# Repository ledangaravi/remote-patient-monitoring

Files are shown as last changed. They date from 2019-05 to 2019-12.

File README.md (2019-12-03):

# Patient24

Welcome to the Patient24 Github Repository. To access detailed documentation about the project, please [go to the wiki](https://github.com/ledangaravi/remote-patient-monitoring/wiki).

## About
Patient24 brings together newly released sensors and state-of-the-art self-charging technology to provide next generation remote patient monitoring.

The Patient24 solution consists of a wearable device accompanied by an Android and an iOS application. [Watch the video](https://www.youtube.com/watch?v=plrVBWvTG4c) below to learn more.

Promotional Video (https://www.youtube.com/watch?v=plrVBWvTG4c)

## Contact
- For all enquiries do not hesitate to [contact us via email](mailto:jf1116@ic.ac.uk).

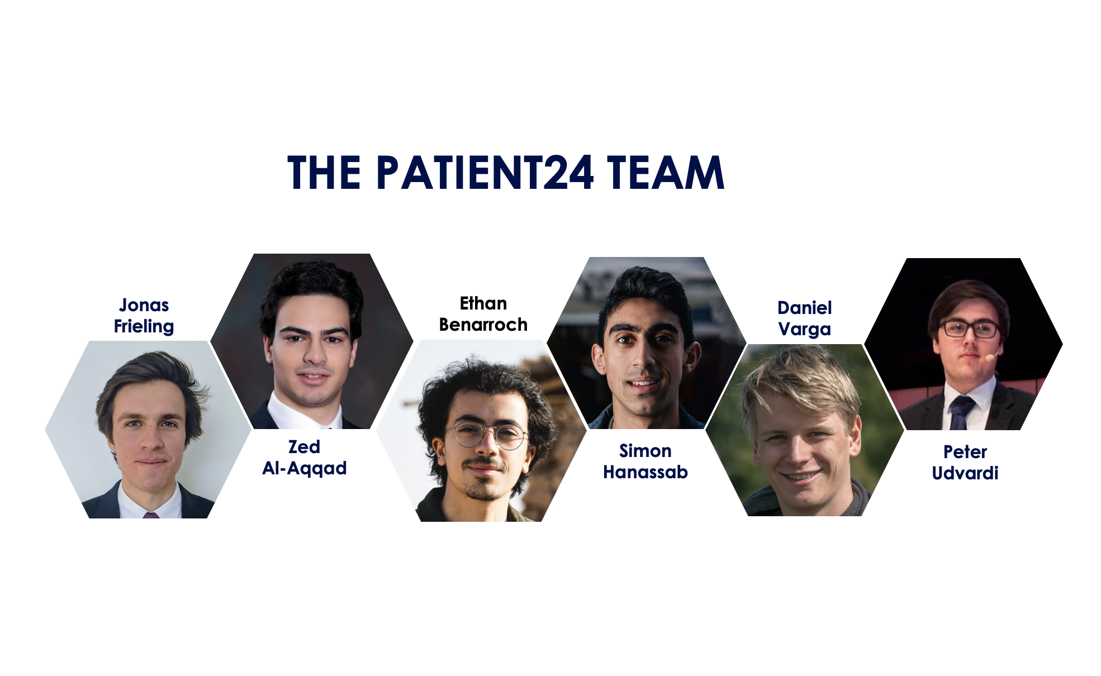
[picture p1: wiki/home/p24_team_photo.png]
Team Photo


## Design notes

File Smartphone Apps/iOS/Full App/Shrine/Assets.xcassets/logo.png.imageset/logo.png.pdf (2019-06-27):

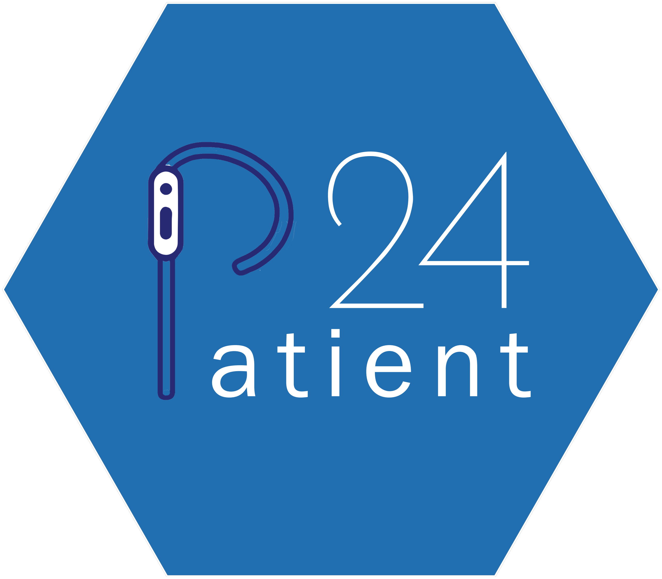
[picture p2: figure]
atient

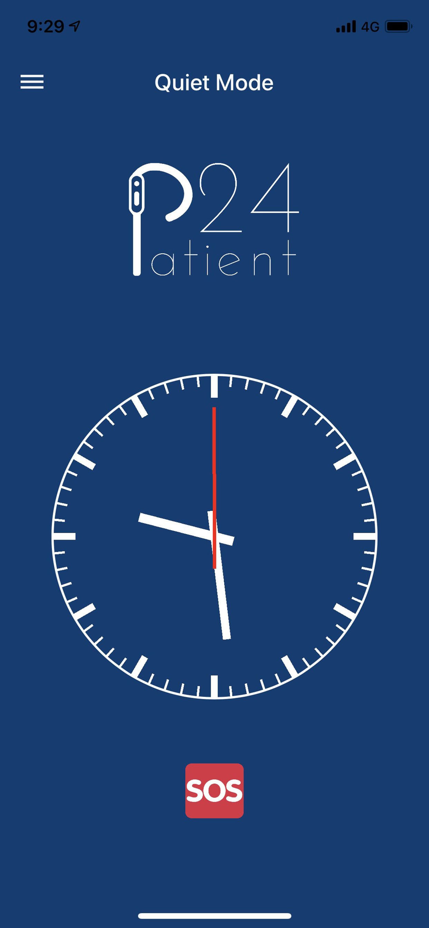
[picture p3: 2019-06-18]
Marketing/poster/images/iphone_screenshot.jpg

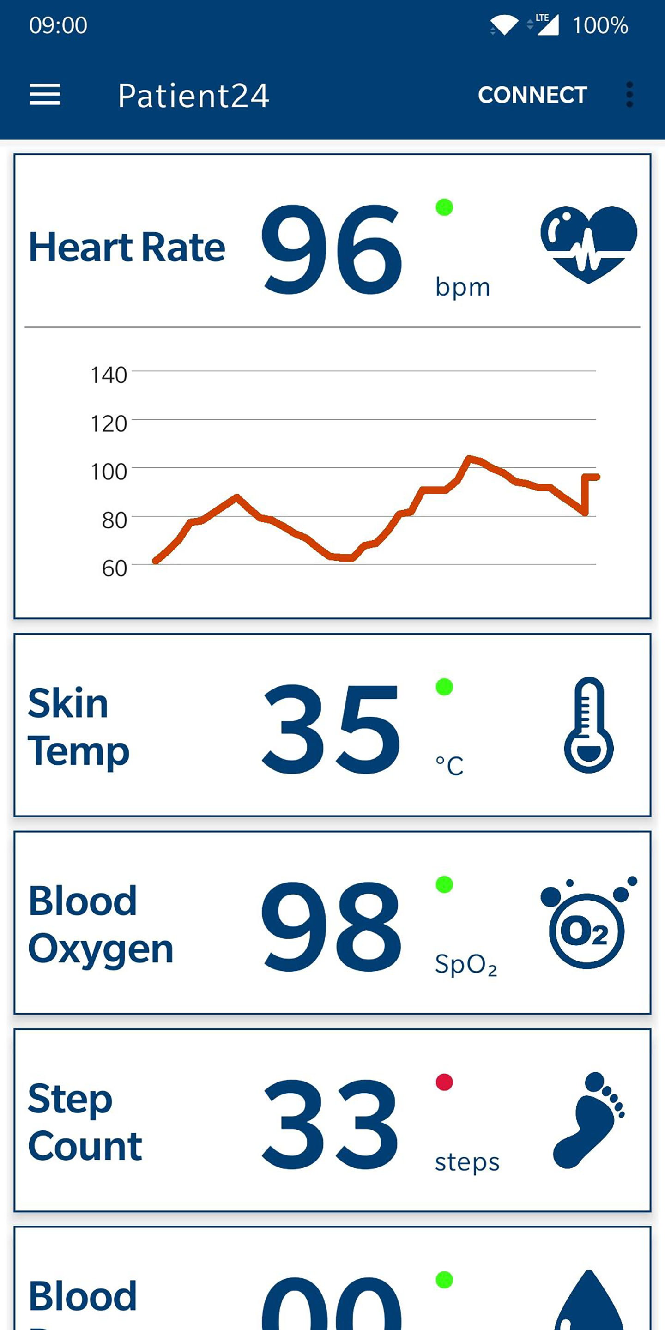
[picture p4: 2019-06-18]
Marketing/poster/images/android.jpg

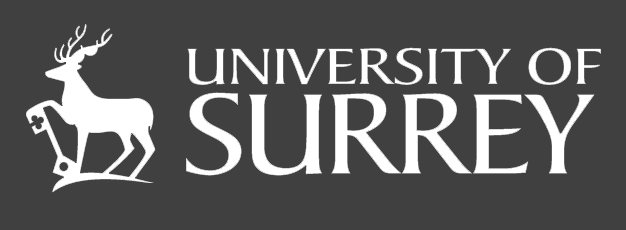
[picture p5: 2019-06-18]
Marketing/poster/images/surrey-Uni.png

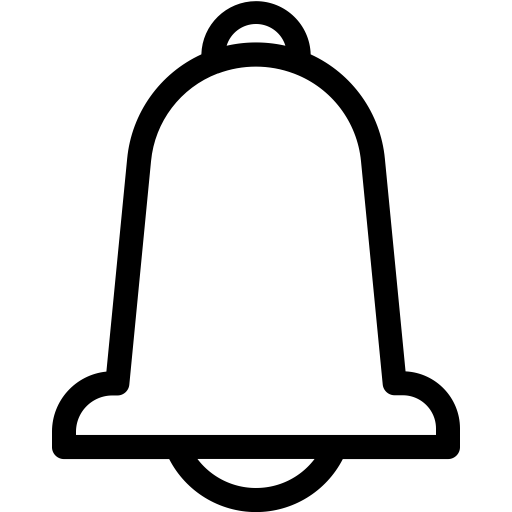
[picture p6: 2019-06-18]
Marketing/poster/images/alert.png

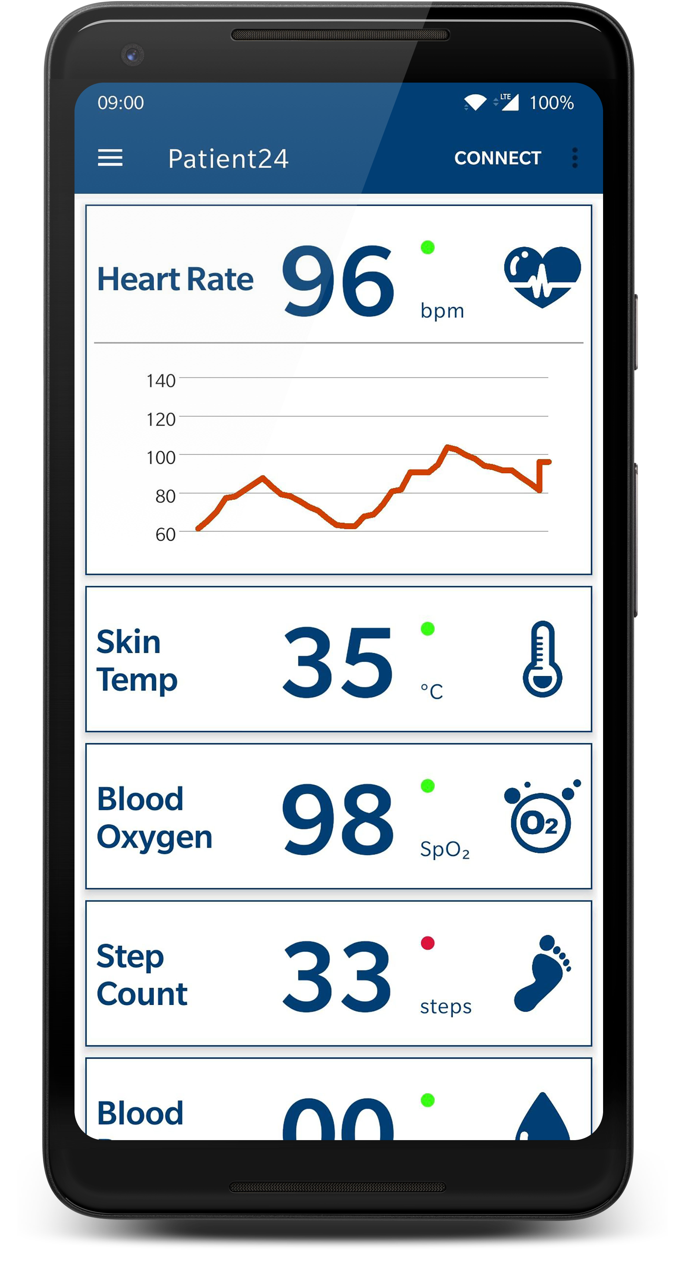
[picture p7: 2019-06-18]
Marketing/poster/images/android_framed.png

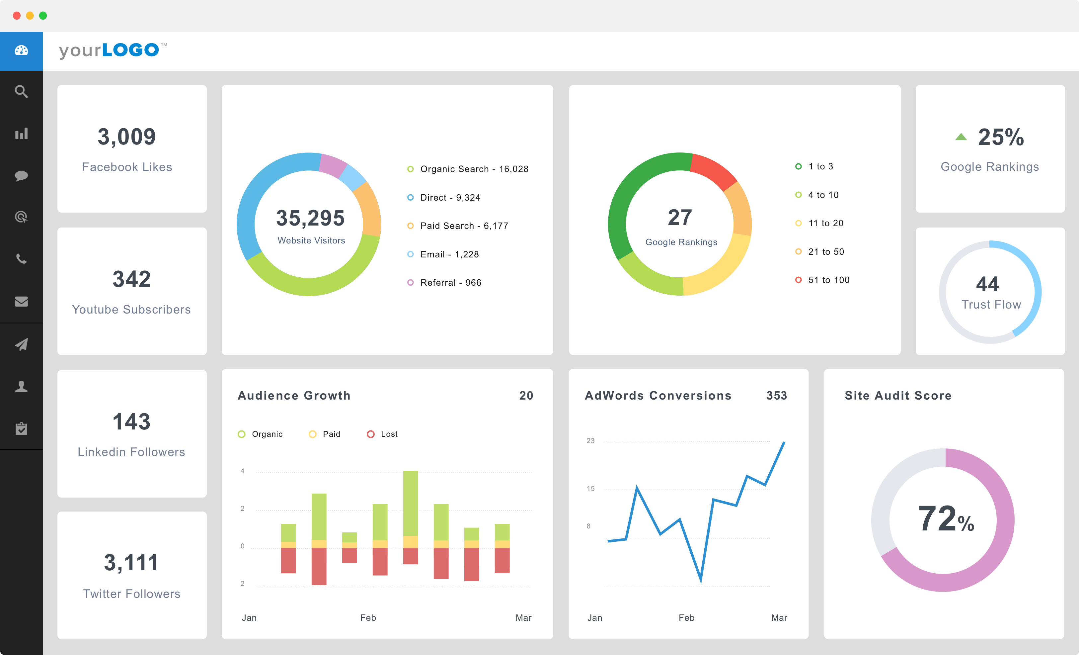
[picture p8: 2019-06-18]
Marketing/poster/images/dashboard.png

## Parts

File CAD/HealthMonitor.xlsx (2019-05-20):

Id | Designator | Package | Quantity | Designation | Tolerance
1 | J6 | USB_C_Receptacle_Amphenol_12401610E4-2A_CircularHoles | 1 | USB_C_Receptacle_USB2.0
2 | U9 | MAX86141ENP | 1 | MAX86141ENP+
4 | D8,D6 | VEMD5010X01 | 2 | VEMD5010X01
6 | U12 | QFN-24-1EP_4x4mm_P0.5mm_EP2.6x2.6mm | 1 | CP2102N-A01-GQFN24
7 | U6 | PQFN50P300X300X86-16N | 1 | LSM6DS33TR
17 | U5 | PQFN70P280X280X100-10N | 1 | BH1792GLC
18 | U10 | TSSOP-8_4.4x3mm_P0.65mm | 1 | AT24CS02-XHM
19 | R32,R23,R24,R25,R35,R33,R11,R10,R9,Rpu1,Rpu2 | R_0402_1005Metric | 11 | 10k
20 | U7 | Texas_R_PUQFN-N12 | 1 | TXB0104RUT
21 | C17,C27 | C_0603_1608Metric | 2 | 22u
23 | C26,C24,C25,C7,C20,C21,C23,C5 | C_0402_1005Metric | 8 | 1u
24 | D7 | LED_PLCC-2 | 1 | LED_LY_P47F-TM
25 | D5 | LED_PLCC-2 | 1 | LED-LT PWSG-AABB-36-46-F
29 | R6 | R_0402_1005Metric | 1 | 1M
30 | U4 | SOT-23-5 | 1 | LD39015M33R
31 | U13 | ADG884BRMZ | 1 | ADG884BRMZ
32 | U2 | ADP5092ACPZ-1-R7 | 1 | ADP5092ACPZ-1-R7
33 | Y1 | XTAL_ABS06-32.768KHZ-T | 1 | ABS06-32.768KHZ-T
34 | C22,C1,C13,C11,C9 | C_0402_1005Metric | 5 | 0.1u
35 | C6,C12,C16 | C_0402_1005Metric | 3 | 4.7u
39 | C14 | C_0402_1005Metric | 1 | 5600p
40 | C15,C2,C3,C10 | C_0402_1005Metric | 4 | 10u
41 | C18,C19 | C_0402_1005Metric | 2 | 12p
47 | D1 | D_0603_1608Metric | 1 | LED_ir
48 | D2,D3 | D_0603_1608Metric | 2 | LED_green
49 | L2 | L_0603_1608Metric | 1 | 4.7u
50 | R20 | R_0402_1005Metric | 1 | 2.4k
51 | R22 | R_0402_1005Metric | 1 | 412k
52 | R26,R27,R29,R30,R28 | R_0402_1005Metric | 5 | 50k
53 | R19,R16 | R_0402_1005Metric | 2 | 3.32M | 1%
54 | R31 | R_0402_1005Metric | 1 | 4.75k
55 | R34 | R_0402_1005Metric | 1 | 6.6k
57 | R21,R17 | R_0402_1005Metric | 2 | 6.65M | 1%
58 | D4 | DIOC0404X01-4N | 1 | SML-LX0404SIUPGUSB
59 | U3 | LTC4079IDD-PBF | 1 | LTC4079IDD-PBF
60 | U1 | MAX17048G+ | 1 | MAX17048G+T10
61 | U8 | MAX1921EUT18&plus_T | 1 | MAX1921EUT18+
62 | C4 | C_0402_1005Metric | 1 | 10n
63 | FB1 | L_0402_1005Metric | 1 | Ferrite_Bead
64 | R13,R12 | R_0402_1005Metric | 2 | 5M | 1%
65 | R14 | R_0402_1005Metric | 1 | 3.01M | 1%
66 | R15 | R_0402_1005Metric | 1 | 6.98M | 1%
67 | R18 | R_0402_1005Metric | 1 | 1.07M | 1%
68 | R7 | R_0402_1005Metric | 1 | 2M | 1%
69 | R8 | R_0402_1005Metric | 1 | 3.3k
70 | R5 | R_0402_1005Metric | 1 | 3.57M | 1%
71 | R4 | R_0402_1005Metric | 1 | 6.49M | 1%
72 | R3,R1 | R_0402_1005Metric | 2 | 4M | 1%
73 | R2 | R_0402_1005Metric | 1 | 55.6k | 1%
74 | L1 | L_0805_2012Metric | 1 | 22u

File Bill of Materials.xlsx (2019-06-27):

Designator | Package | Quantity | Designation | Model Number | Supplier | College Discount? | Unit Price (inc VAT) | Unit Price (exc VAT) | Total Quantity with Discount applied (exc VAT) | Scaled Unit Price (inc VAT) | Scaled with Total Quantity & Discounts
C12,C16,C6 | C_0402_1005Metric | 3 | 4.7uF | C1005X5R0J475M050BC | Farnell | 19% | £0.1960 | £0.1568 | £0.3810 | £0.0267 | £0.0649
C14 | C_0402_1005Metric | 1 | 5600pF | MC0402B562K160CT | Farnell | 19% | £0.0090 | £0.0072 | £0.0058 | £0.0033 | £0.0027
C15,C2,C3 | C_0402_1005Metric | 3 | 10uF | GRM155R60J106ME44D | Farnell | 19% | £0.8320 | £0.6656 | £1.6174 | £0.0757 | £0.1840
C17,C27 | C_0603_1608Metric | 2 | 22uF | GRM188R61A226ME15D | Farnell | 19% | £0.2300 | £0.1840 | £0.2981 | £0.0433 | £0.0701
C22,C13,C11, C10, C9, C1 | C_0402_1005Metric | 6 | 0.1uF | 0402YC104KAT2A | Farnell | 19% | £0.0404 | £0.0323 | £0.1571 | £0.0061 | £0.0296
C29,C30,C18,C19 | C_0402_1005Metric | 4 | 12pF | MC0402N120J500CT | Farnell | 19% | £0.0209 | £0.0167 | £0.0542 | £0.0033 | £0.0107
C4 | C_0402_1005Metric | 1 | 10nF | 04023C103KAT2A | Farnell | 19% | £0.0352 | £0.0282 | £0.0228 | £0.0051 | £0.0041
C7,C20,C21,C23,C26,C8,C28,C24,C25,C5 | C_0402_1005Metric | 10 | 1uF | 0402ZD105KAT2A | Farnell | 19% | £0.1840 | £0.1472 | £1.1923 | £0.0423 | £0.3426
D1 | D_0603_1608Metric | 1 | LED_ir | TAN1111C | RS | 19% | £0.1000 | £0.0800 | £0.0648 | £0.0568 | £0.0460
D2,D3 | D_0603_1608Metric | 2 | LED_green | 404-1005-1-ND | DigiKey | 0% | £0.6400 | £0.5120 | £1.0240 | £0.0780 | £0.1560
D4 | DIOC0404X01-4N | 1 | SML-LX0404SIUPGUSB | SML-LX0404SIUPGUSB | Mouser | 0% | £0.7850 | £0.6280 | £0.6280 | £0.2310 | £0.2310
D5 | LED_PLCC-2 | 1 | LED-LT PWSG-AABB-36-46-F | VAOL-S2YP4 | Mouser | 0% | £0.4190 | £0.3352 | £0.3352 | £0.1290 | £0.1290
D7 | LED_PLCC-2 | 1 | LED_LY_P47F-TM | LT T66G-BBDA-29-0-20-R33-Z | DigiKey | 0% | £0.4700 | £0.3760 | £0.3760 | £0.1600 | £0.1600
D8,D6 | VEMD5010X01 | 2 | VEMD5010X01 | VEMD5010X01 | RS | 19% | £0.5200 | £0.4160 | £0.6739 | £0.3064 | £0.4964
FB1 | L_0402_1005Metric | 1 | Ferrite_Bead | MPZ1005A331ETD25 | Mouser | 0% | £0.1830 | £0.1464 | £0.1464 | £0.0480 | £0.0480
J27 | Molex - 51281-0594-MOLEX_51281-0594_0 | 1 | 51281-0594 | 51281-0594 | Farnell | 19% | £0.3100 | £0.2480 | £0.2009 | £0.1600 | £0.1296
J6 | USB_C_Receptacle_Amphenol_12401610E4-2A | 1 | USB_C_Receptacle_USB2.0 | 12401610E4#2A | Mouser | 0% | £1.6400 | £1.3120 | £1.3120 | £0.9350 | £0.9350
L1 | L_0805_2012Metric | 1 | 22uH | MLZ2012M220WT000 | Mouser | 0% | £0.1070 | £0.0856 | £0.0856 | £0.0280 | £0.0280
L2 | L_0603_1608Metric | 1 | 4.7uH | KLZ1608MHR4R7WTD25 | Mouser | 0% | £0.1900 | £0.1520 | £0.1520 | £0.0540 | £0.0540
R13,R12 | R_0402_1005Metric | 2 | 4.99MΩ | CRCW04024M99FKEDC | Mouser | 0% | £0.1000 | £0.0800 | £0.1600 | £0.0030 | £0.0060
R14 | R_0402_1005Metric | 1 | 3.01MΩ | CRCW04023M01FKED | Farnell | 19% | £0.0091 | £0.0073 | £0.0059 | £0.0020 | £0.0016
R15 | R_0402_1005Metric | 1 | 6.98MΩ | CRCW04026M98FKED | Mouser | 0% | £0.0760 | £0.0608 | £0.0608 | £0.0030 | £0.0030
R18 | R_0402_1005Metric | 1 | 1.07MΩ | RC0402FR-071M07L | Mouser | 0% | £0.0760 | £0.0608 | £0.0608 | £0.0030 | £0.0030
R19,R16 | R_0402_1005Metric | 2 | 3.32MΩ | CRCW04023M32FKED | Mouser | 0% | £0.0720 | £0.0576 | £0.1152 | £0.0030 | £0.0060
R2 | R_0402_1005Metric | 1 | 56kΩ | CRCW04023M32FKED | Farnell | 19% | £0.0760 | £0.0608 | £0.0492 | £0.0030 | £0.0024
R20 | R_0402_1005Metric | 1 | 2.4kΩ | CRCW04022K40FKED | Farnell | 19% | £0.0168 | £0.0134 | £0.0109 | £0.0035 | £0.0028
R21,R17 | R_0402_1005Metric | 2 | 6.65MΩ | CRCW04026M65FKED | Farnell | 19% | £0.0119 | £0.0095 | £0.0154 | £0.0033 | £0.0053
R22 | R_0402_1005Metric | 1 | 412kΩ | CRCW0402412KFKED | Farnell | 19% | £0.0166 | £0.0133 | £0.0108 | £0.0035 | £0.0028
R26,R27,R29,R30,R28 | R_0402_1005Metric | 5 | 50kΩ | CRCW040250K0FKED | Mouser | 0% | £0.4190 | £0.3352 | £1.6760 | £0.0810 | £0.4050
R3,R1 | R_0402_1005Metric | 2 | 4MΩ | CRCW04023M92FKED | Mouser | 0% | £0.0760 | £0.0608 | £0.1216 | £0.0030 | £0.0060
R31 | R_0402_1005Metric | 1 | 4.75kΩ | CRCW04024K75FKED | Farnell | 19% | £0.0089 | £0.0071 | £0.0058 | £0.0044 | £0.0036
R33,R24,R25,R32,R23,R35,R11,R10,R9, Rpu1, Rpu2 | R_0402_1005Metric | 11 | 10kΩ | CRCW040210K0FKEDHP | Farnell | 19% | £0.0418 | £0.0334 | £0.2980 | £0.0099 | £0.0882
R34 | R_0402_1005Metric | 1 | 6.65kΩ | MCWR04X6651FTL | Farnell | 19% | £0.0041 | £0.0033 | £0.0027 | £0.0006 | £0.0005
R4 | R_0402_1005Metric | 1 | 6.49MΩ | RC0402FR-076M49L | Mouser | 0% | £0.0760 | £0.0608 | £0.0608 | £0.0020 | £0.0020
R5 | R_0402_1005Metric | 1 | 3.57M | CRCW04023M57FKED | Farnell | 19% | £0.0088 | £0.0070 | £0.0057 | £0.0027 | £0.0022
R6 | R_0402_1005Metric | 1 | 1MΩ | MCMR04X1004FTL | Farnell | 19% | £0.0085 | £0.0068 | £0.0055 | £0.0013 | £0.0011
R7 | R_0402_1005Metric | 1 | 2MΩ | CRCW04022M00FKED | Farnell | 19% | £0.0168 | £0.0134 | £0.0109 | £0.0035 | £0.0028
R8 | R_0402_1005Metric | 1 | 3.3kΩ | CRCW04023K30FKED | Farnell | 19% | £0.0146 | £0.0117 | £0.0095 | £0.0031 | £0.0025
U1 | MAX17048G+ | 1 | MAX17048G+T10 | MAX17048G+T10 | Farnell | 19% | £1.9100 | £1.5280 | £1.2377 | £0.9340 | £0.7565
U10 | TSSOP-8_4.4x3mm_P0.65mm | 1 | AT24CS02-XHM | AT24CS02-XHM | Mouser | 0% | £0.1680 | £0.1344 | £0.1344 | £0.1650 | £0.1650
U11 | BT832-BT832L | 1 | BT832L | BT832L | Mouser | 0% | £7.2600 | £5.8080 | £5.8080 | £3.8900 | £3.8900
U12 | QFN-24-1EP_4x4mm_P0.5mm_EP2.6x2.6mm | 1 | CP2102N-A01-GQFN24 | CP2102N-A01-GQFN24 | Farnell | 19% | £1.2400 | £0.9920 | £0.8035 | £0.9320 | £0.7549
U13 | ADG884BRMZ | 1 | ADG884BRMZ | ADG884BRMZ | Farnell | 19% | £2.4800 | £1.9840 | £1.6070 | £1.2400 | £1.0044
U14,U4 | SOT-23-5 | 2 | LD39015M33R | LD39015M33R | Farnell | 19% | £0.6860 | £0.5488 | £0.8891 | £0.2810 | £0.4552
U2 | ADP5092ACPZ-1-R7 | 1 | ADP5092ACPZ-1-R7 | ADP5092ACPZ-1-R7 | Farnell | 19% | £2.5200 | £2.0160 | £1.6330 | £2.4000 | £1.9440
U3 | LTC4079IDD-PBF | 1 | LTC4079IDD-PBF | LTC4079IDD-PBF | Mouser | 0% | £5.0000 | £4.0000 | £4.0000 | £2.5400 | £2.5400
U5 | PQFN70P280X280X100-10N | 1 | BH1792GLC | BH1792GLC | Mouser | 0% | £8.1500 | £6.5200 | £6.5200 | £4.2900 | £4.2900
U6 | PQFN50P300X250X86-14N | 1 | LSM6DSLTR | LSM6DSLTR | Mouser | 0% | £3.0400 | £2.4320 | £2.4320 | £1.4900 | £1.4900
U7 | Texas_R_PUQFN-N12 | 1 | TXB0104RUT | TXB0104RUT | Mouser | 0% | £1.0600 | £0.8480 | £0.8480 | £0.4230 | £0.4230
U8 | MAX1921EUT18&plus_T | 1 | MAX1921EUT18+ | MAX1921EUT18+ | Farnell | 19% | £2.3300 | £1.8640 | £1.5098 | £1.3300 | £1.0773
U9 | MAX86141ENP | 1 | MAX86141ENP+ | MAX86141ENP+ | Farnell | 19% | £5.8900 | £4.7120 | £3.8167 | £2.9300 | £2.3733
X1 | LiPo Battery | 1 | LP-402025-IS-3 | LP-402025-IS-3 | Farnell | 19% | £15.3300 | £12.2640 | £9.9338 | £6.5700 | £5.3217
X2 | Peltier Module | 1 | CP-85138 | CP-85138 | Mouser | 0% | £11.4400 | £9.1520 | £9.1520 | £9.0900 | £9.0900
X3 | Heat Sink | 1 | MPC151525T | MPC151525T | Farnell | 19% | £1.7700 | £1.4160 | £1.1470 | £0.6280 | £0.5087
Y1 | XTAL_ABS06-32.768KHZ-T | 1 | ABS06-32.768KHZ-T | ABS06-32.768KHZ-T | Farnell | 19% | £1.2100 | £0.9680 | £0.7841 | £0.5470 | £0.4431
 |  |  |  |  |  |  | £79.52 | £63.62 | £63.67 | £42.21 | £40.20
NB: Prices valid as of 22/06/2019 |  |  |  |  |  |  |  |  |  |  | exc VAT:
 |  |  |  |  |  |  |  |  |  |  | £32.16

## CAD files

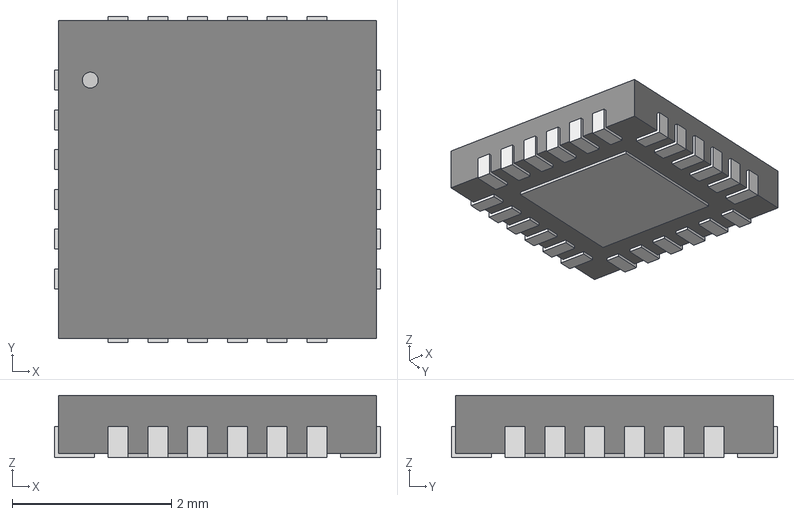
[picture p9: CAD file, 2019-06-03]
CAD/3dmodels/ADP5092.step
4.10 x 4.10 x 0.783 mm

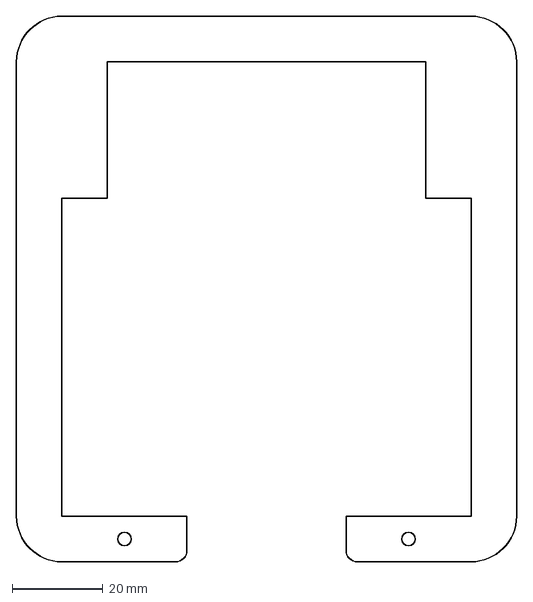
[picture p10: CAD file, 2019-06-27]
PCB/bracket/bracket_top.dxf
110.0 x 120.0 mm

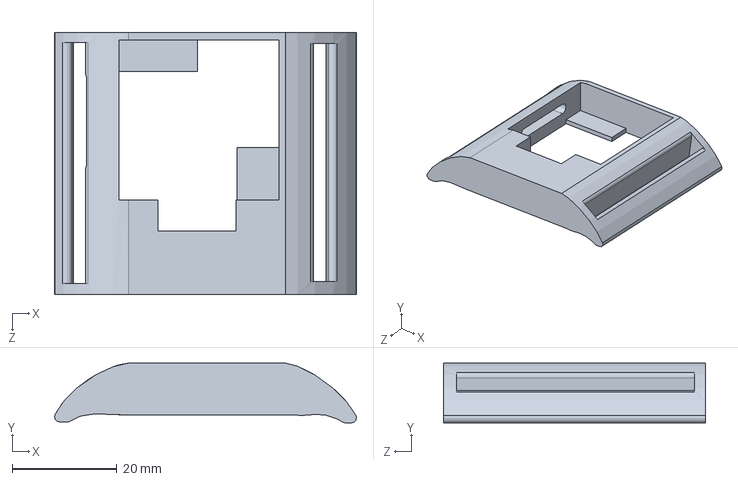
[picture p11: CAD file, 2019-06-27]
Strap Design/Solidworks Files/Version5_SensorPCB.SLDPRT
57.6 x 11.4 x 50.0 mm

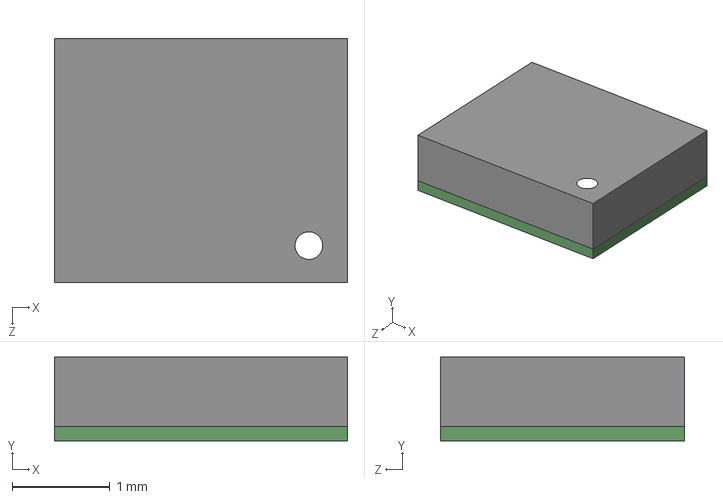
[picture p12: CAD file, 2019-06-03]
CAD/3dmodels/LSM6DS3--3DModel-STEP-56544.STEP
3.00 x 0.86 x 2.50 mm

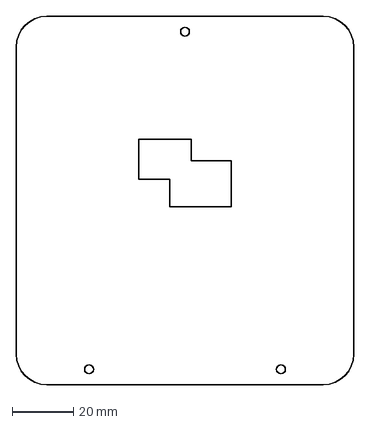
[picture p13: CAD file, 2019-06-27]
PCB/bracket/bracket_bottom.dxf
110.0 x 120.0 mm

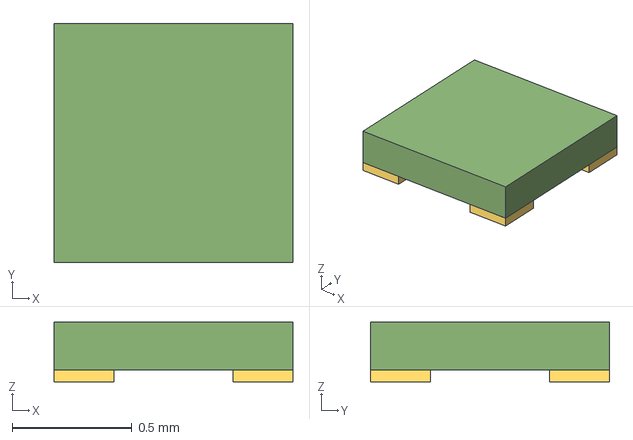
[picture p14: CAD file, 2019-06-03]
CAD/3dmodels/LMS_XL0404.step
1.00 x 1.00 x 0.25 mm

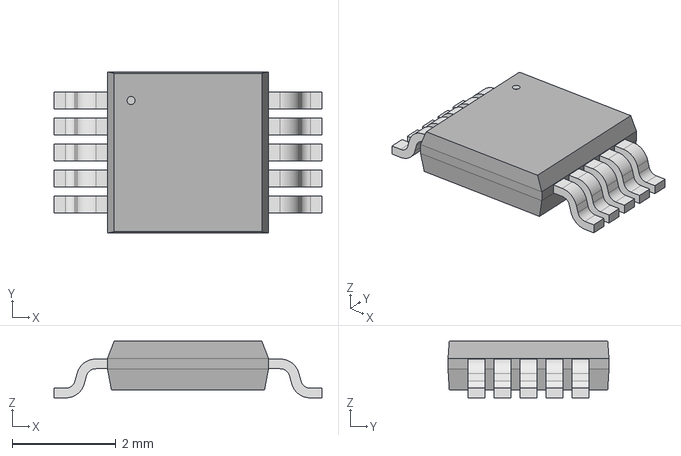
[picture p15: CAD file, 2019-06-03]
CAD/3dmodels/ADG884BRMZ.step
5.16 x 3.10 x 1.09 mm

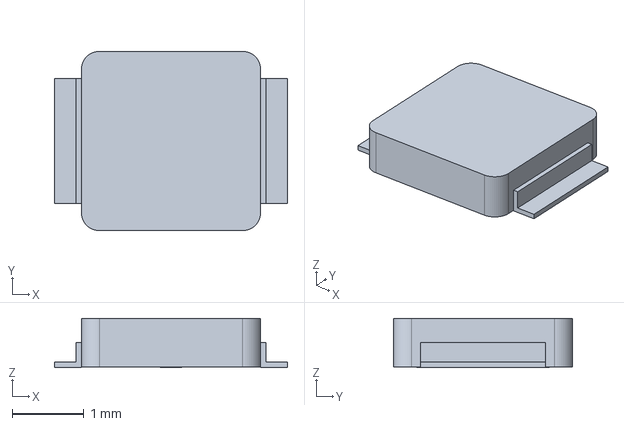
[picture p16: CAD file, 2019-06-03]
CAD/3dmodels/LED_LY_P47F-v2.step
3.25 x 2.50 x 0.685 mm

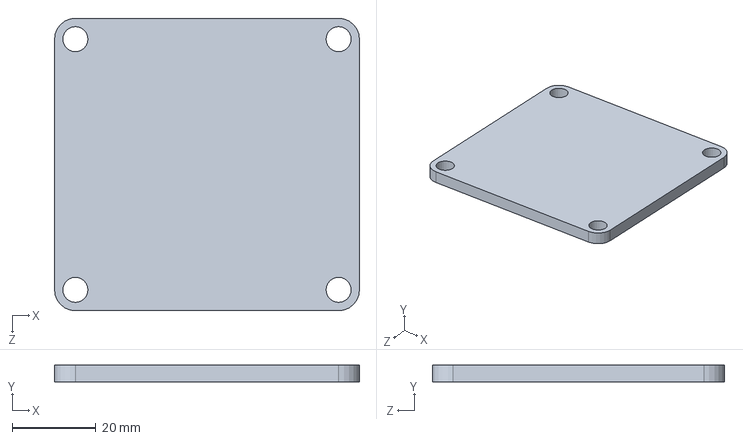
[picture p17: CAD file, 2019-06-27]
Strap Design/Solidworks Files/Mould4_BatteryTop.SLDPRT
73.0 x 4.00 x 70.0 mm

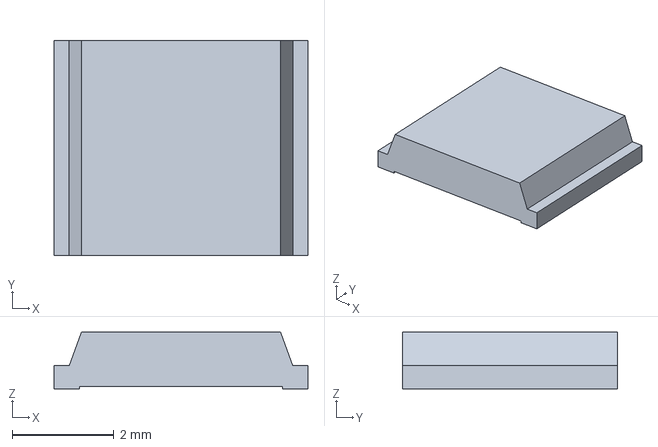
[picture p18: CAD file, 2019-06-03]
CAD/3dmodels/VEMD5010.step
5.00 x 4.24 x 1.12 mm

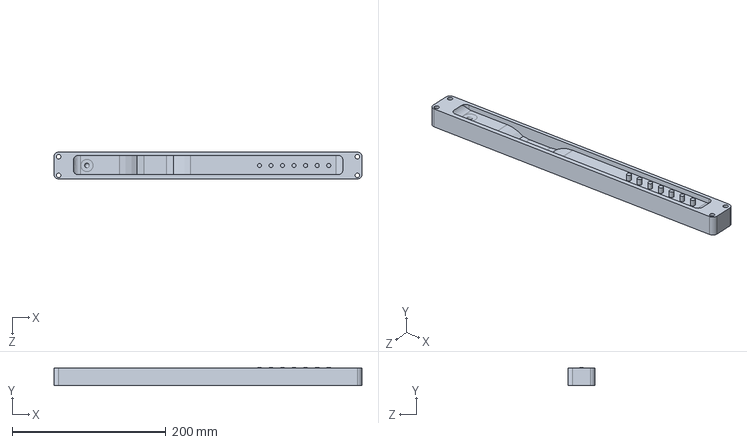
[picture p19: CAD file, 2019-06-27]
Strap Design/Solidworks Files/Mould1_part1.SLDPRT
400.0 x 24.0 x 35.0 mm

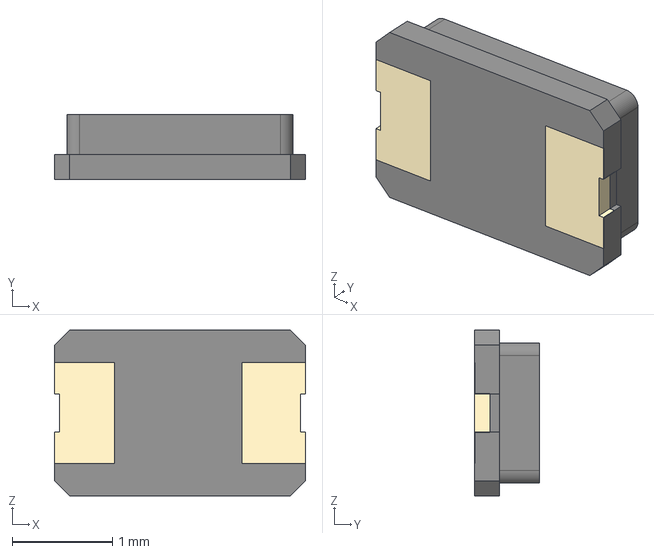
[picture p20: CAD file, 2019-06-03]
CAD/3dmodels/ABS06-v2.step
2.50 x 0.648 x 1.65 mm

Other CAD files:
Strap Design/Solidworks Files/Mould2_part1.SLDPRT
Strap Design/Solidworks Files/Mould1_part2.SLDPRT
Strap Design/Solidworks Files/Mould4_SensorBottom.SLDPRT
Strap Design/Solidworks Files/Mould3_part2.SLDPRT
Strap Design/Solidworks Files/Mould4_SensorTop.SLDPRT
CAD/3dmodels/BT832L.STEP
CAD/3dmodels/LTC4079.step
CAD/3dmodels/MAX86141.step
CAD/3dmodels/max1921.step
Strap Design/Solidworks Files/Mould2_part2.SLDPRT
Strap Design/Solidworks Files/Mould3_part1.SLDPRT
Strap Design/Solidworks Files/Mould4_BatteryBottom.SLDPRT
Strap Design/Solidworks Files/SENSORMODULEP24.SLDDRW
Strap Design/Solidworks Files/Version5_Batt,Peltier,PowerPCB.SLDPRT
Strap Design/Solidworks Files/Version6_powerModule.SLDPRT
Strap Design/Solidworks Files/Version6_sensorModule.SLDPRT
Strap Design/Solidworks Files/powPCB+peletierbattVersion5flat.SLDDRW

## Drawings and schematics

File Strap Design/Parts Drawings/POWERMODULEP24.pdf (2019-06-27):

2 1

B

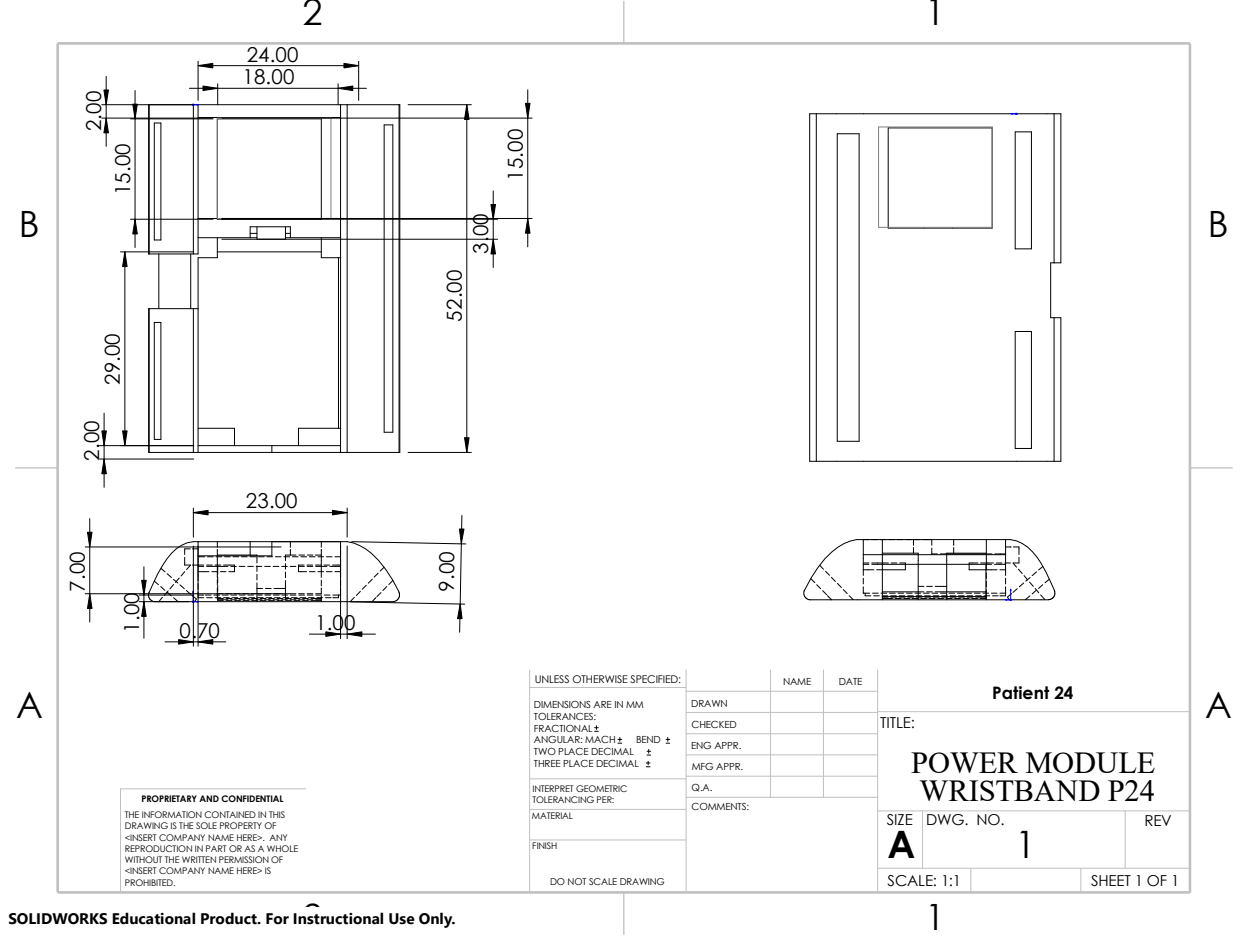
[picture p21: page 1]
SIZE; BEND; DWG. NO.; A DRAWN; COMMENTS:; PROHIBITED.; SHEET 1 OF 1; DATE; MATERIAL; NAME; REV; DO NOT SCALE DRAWING; SCALE: 1:1; FINISH; Patient 24

UNLESS OTHERWISE SPECIFIED:

DIMENSIONS ARE IN MM
TOLERANCES:
FRACTIONAL
ANGULAR: MACH
TWO PLACE DECIMAL

CHECKED | | TITLE: WRISTBAND P24

MFG APPR. | | POWER MODULE THREE PLACE DECIMAL

ENG APPR.

INTERPRET GEOMETRIC TOLERANCING PER: | Q.A.

PROPRIETARY AND CONFIDENTIAL
THE INFORMATION CONTAINED IN THIS
DRAWING IS THE SOLE PROPERTY OF
<INSERT COMPANY NAME HERE>. ANY
REPRODUCTION IN PART OR AS A WHOLE
WITHOUT THE WRITTEN PERMISSION OF
<INSERT COMPANY NAME HERE> IS

SOLIDWORKS Educational Product. For Instructional Use Only.

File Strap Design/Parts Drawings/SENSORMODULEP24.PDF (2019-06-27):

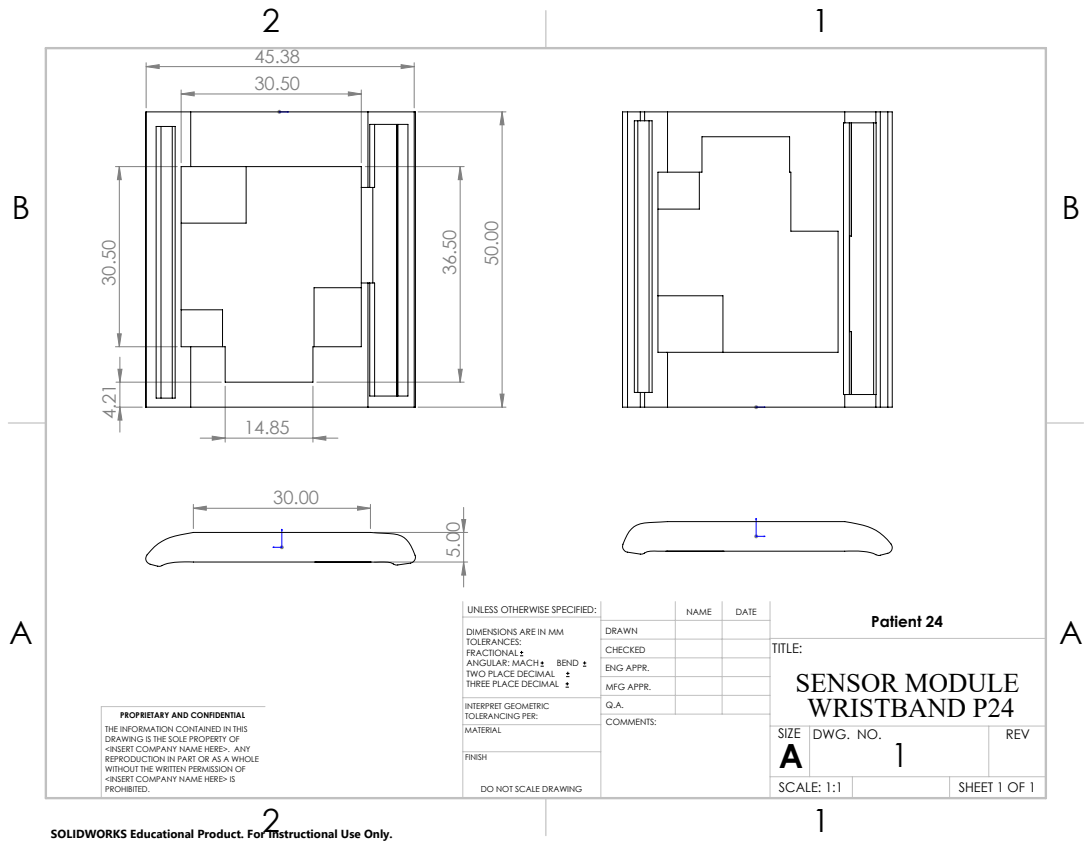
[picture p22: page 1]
DWG. NO.; DO NOT SCALE DRAWING; SCALE: 1:1; SHEET 1 OF 1; Patient 24

UNLESS OTHERWISE SPECIFIED:

DIMENSIONS ARE IN MM TOLERANCES: FRACTIONAL ANGULAR: MACH BEND TWO PLACE DECIMAL THREE PLACE DECIMAL | DRAWN

CHECKED | | TITLE: SENSOR MODULE WRISTBAND P24

ENG APPR.
MFG APPR.

INTERPRET GEOMETRIC TOLERANCING PER: | Q.A.

PROPRIETARY AND CONFIDENTIAL
THE INFORMATION CONTAINED IN THIS
DRAWING IS THE SOLE PROPERTY OF
<INSERT COMPANY NAME HERE>. ANY
REPRODUCTION IN PART OR AS A WHOLE
WITHOUT THE WRITTEN PERMISSION OF
<INSERT COMPANY NAME HERE> IS
PROHIBITED.

SOLIDWORKS Educational Product. For Instructional Use Only.

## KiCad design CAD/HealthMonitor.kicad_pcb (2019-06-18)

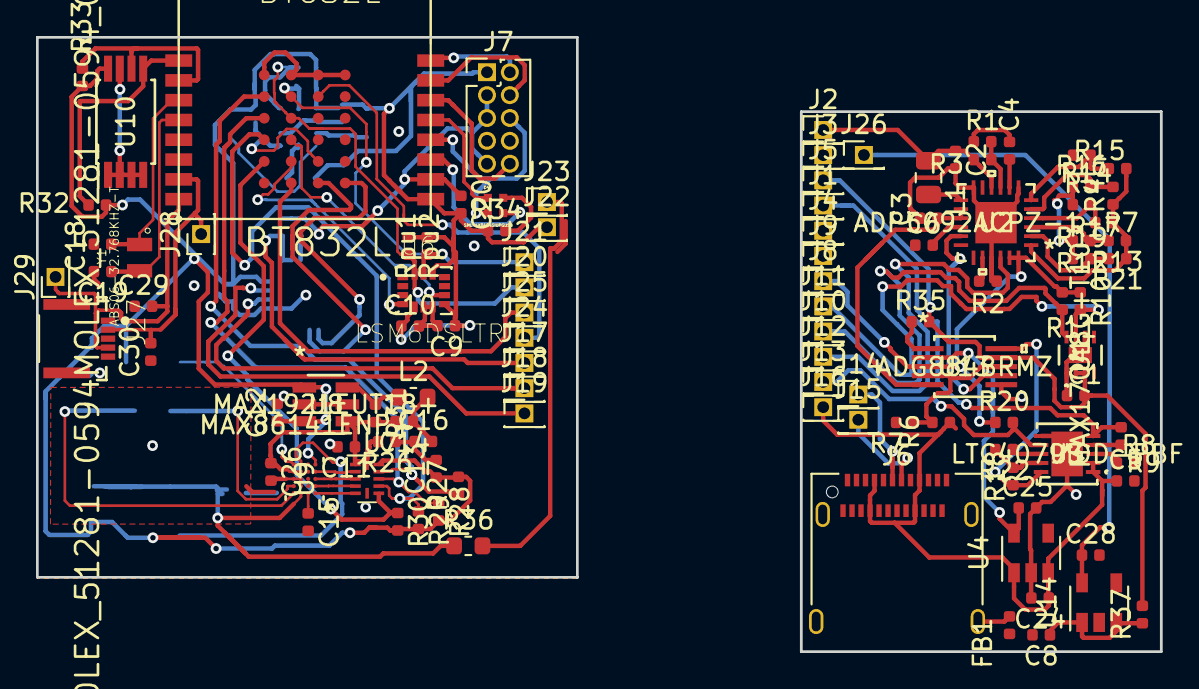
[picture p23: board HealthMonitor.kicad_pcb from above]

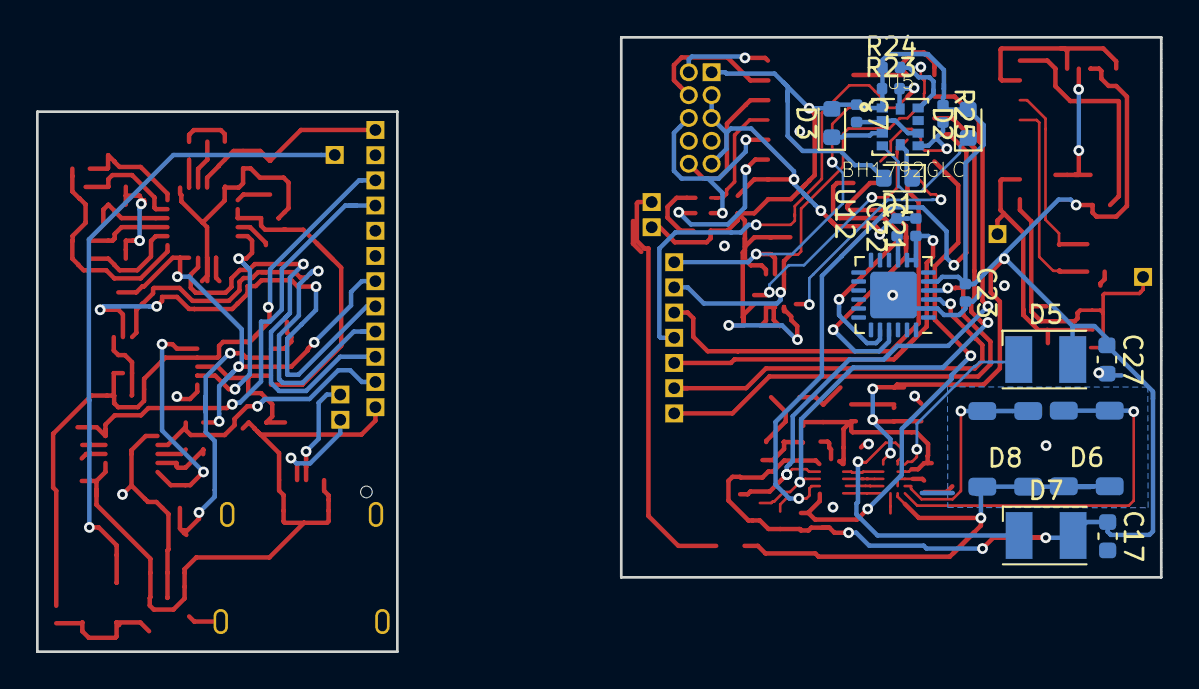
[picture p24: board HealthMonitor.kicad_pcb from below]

Board: 2 copper layers, 62.4 x 34.1 mm, 124 parts (18 on the bottom side), 76 nets.

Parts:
C1, C11, C13, C22: 0.1u; C_0402_1005Metric
C2, C3, C15: 10u; C_0402_1005Metric
C4: 10n; C_0402_1005Metric
C5, C7, C8, C20, C21, C23, C24, C25, C26, C28: 1u; C_0402_1005Metric
C6, C12, C16: 4.7u; C_0402_1005Metric
C9, C10: 100nF; C_0402_1005Metric
C14: 5600p; C_0402_1005Metric
C17, C27: 22u; C_0603_1608Metric
C18, C19, C29, C30: 12p; C_0402_1005Metric
D1: LED_ir; D_0603_1608Metric
D2, D3: LED_green; D_0603_1608Metric
D4: SML-LX0404SIUPGUSB; DIOC0404X01-4N
D5: LED-LT PWSG-AABB-36-46-F; LED_PLCC-2
D6, D8: VEMD5010X01
D7: LED_LY_P47F-TM; LED_PLCC-2
FB1: Ferrite_Bead; L_0402_1005Metric
J1: BAT_T; PinHeader_1x01_P1.27mm_Vertical
J2: TEG+; PinHeader_1x01_P1.27mm_Vertical
J3: TEG-; PinHeader_1x01_P1.27mm_Vertical
J4: BAT-; PinHeader_1x01_P1.27mm_Vertical
J5: BAT+; PinHeader_1x01_P1.27mm_Vertical
J6: USB_C_Receptacle_USB2.0; USB_C_Receptacle_Amphenol_12401610E4-2A
J7: Conn_02x05_Odd_Even; PinHeader_2x05_P1.27mm_Vertical
J8, J22: VCC; PinHeader_1x01_P1.27mm_Vertical
J9, J23: GND; PinHeader_1x01_P1.27mm_Vertical
J10, J20: SDA; PinHeader_1x01_P1.27mm_Vertical
J11, J21: SCL; PinHeader_1x01_P1.27mm_Vertical
J12, J25: DIS_SW; PinHeader_1x01_P1.27mm_Vertical
J13, J24: BAT_CHRG; PinHeader_1x01_P1.27mm_Vertical
J14: USBDP; PinHeader_1x01_P1.27mm_Vertical
J15: USBDM; PinHeader_1x01_P1.27mm_Vertical
J16: USB_V; PinHeader_1x01_P1.27mm_Vertical
J17: VBUS; PinHeader_1x01_P1.27mm_Vertical
J18: D+; PinHeader_1x01_P1.27mm_Vertical
J19: D-; PinHeader_1x01_P1.27mm_Vertical
J26, J28, J29: Conn_01x01_Male; PinHeader_1x01_P1.27mm_Vertical
J27: MOLEX_51281-0594MOLEX_51281-0594_0_0; Molex - 51281-0594-MOLEX_51281-0594_0
L1: 22u; L_0805_2012Metric
L2: 4.7u; L_0603_1608Metric
R1, R3: 4M; R_0402_1005Metric
R2: 55.6k; R_0402_1005Metric
R4: 6.49M; R_0402_1005Metric
R5: 3.57M; R_0402_1005Metric
R6: 1M; R_0402_1005Metric
R7: 2M; R_0402_1005Metric
R8: 3.3k; R_0402_1005Metric
R9, R10, R11, R23, R24, R25, R32, R33, R35: 10k; R_0402_1005Metric
R12, R13: 5M; R_0402_1005Metric
R14: 3.01M; R_0402_1005Metric
R15: 6.98M; R_0402_1005Metric
R16, R19: 3.32M; R_0402_1005Metric
R17, R21: 6.65M; R_0402_1005Metric
R18: 1.07M; R_0402_1005Metric
R20: 2.4k; R_0402_1005Metric
R22: 412k; R_0402_1005Metric
R26, R27, R28, R29, R30: 50k; R_0402_1005Metric
R31: 4.75k; R_0402_1005Metric
R34: 6.6k; R_0402_1005Metric
R36: 0; R_0603_1608Metric
R37: 0; R_0402_1005Metric
Rpu1, Rpu2: 10kOhms; R_0402_1005Metric
U1: MAX17048G+T10; MAX17048G+
U2: ADP5092ACPZ-1-R7
U3: LTC4079IDD-PBF
U4, U14: LD39015M33R; SOT-23-5
U5: BH1792GLC; PQFN70P280X280X100-10N
U6: LSM6DSLTR; PQFN50P300X250X86-14N
U7: TXB0104RUT; Texas_R_PUQFN-N12
U8: MAX1921EUT18+; MAX1921EUT18&plus_T
U9: MAX86141ENP+; MAX86141ENP
U10: AT24CS02-XHM; TSSOP-8_4.4x3mm_P0.65mm
U11: BT832L; BT832-BT832L
U12: CP2102N-A01-GQFN24; QFN-24-1EP_4x4mm_P0.5mm_EP2.6x2.6mm
U13: ADG884BRMZ
Y1: ABS06-32.768KHZ-T; XTAL_ABS06-32.768KHZ-T

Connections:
+3V3: C7.1, C9.1, C10.1, C12.1, C13.1, C17.1, C20.2, C23.1, C27.1, D1.2, D2.2, D3.2, D5.2, D7.2, J7.1, J8.1, J22.1, R10.1, R11.1, R20.1, R23.1, R24.1, R25.1, R27.2, R28.2, R29.2, R30.2, R32.1, R33.1, R34.1, Rpu1.2, Rpu2.1, U2.23, U2.24, U5.1, U6.5, U6.8, U6.12, U7.11, U8.1, U8.3, U9.A1, U10.8, U11.P$9, U12.5, U13.3
/BAT_CHRG: J13.1, J24.1, R20.2, U3.7, U11.P$C1
/BVP_INT: R25.2, U5.6, U11.P$C4
/DIS_SW: J12.1, J25.1, U2.22, U11.P$B5
/IMU_INT1: U6.9, U11.P$B3
/IMU_INT2: U6.4, U11.P$B4
/MaxSensorComplete/1.8V: C11.1, C14.2, C26.1, R31.2, U7.1, U8.4, U9.C2, U9.D2
/MaxSensorComplete/CSB: U7.5, U9.A5
/MaxSensorComplete/SCLK: U7.2, U9.A2
/MaxSensorComplete/SDI: U7.4, U9.A4
/MaxSensorComplete/SDO: U7.3, U9.A3
/SCL: J11.1, J21.1, R10.2, R23.2, Rpu1.1, U1.7, U5.10, U6.13, U11.P$B1
/SDA: J10.1, J20.1, R11.2, R24.2, Rpu2.2, U1.8, U5.9, U6.14, U11.P$B2
/SoC/CSB: R30.1, U7.7, U11.P$A4
/SoC/P18: D4.3, J7.6, U11.P$12
/SoC/P21: J7.10, U11.P$14
/SoC/SCLK: R27.1, U7.10, U11.P$A1
/SoC/SDI: R29.1, U7.8, U11.P$A3
/SoC/SDO: R28.1, U7.9, U11.P$A2
/SoC/SWCLK: J7.4, U11.P$15
/SoC/SWDIO: J7.2, U11.P$16
/power/BAT+: C1.2, J5.1, R35.2, R37.2, U1.2, U1.3, U13.9
/power/BAT_EH: U2.17, U13.7
/power/BAT_T: J1.1, R9.2, U3.5
/power/BAT_USB: R18.2, U3.10, U13.10
/power/B_CONN: R6.2, R7.1, U13.4, U13.8
/power/EH_3v3: C3.1, U2.14, U2.15, U13.5
/power/REF: R4.2, R13.1, R15.1, R17.1, R21.1, U2.1
/power/TEG+: C2.1, J2.1, L1.2, R3.2, U2.10
/power/USB_3v3: C25.1, U4.5, U13.2
/power/USB_VBUS: C5.1, C21.1, C24.1, J6.A4, J6.A9, J6.B4, J6.B9, J16.1, J17.1, R6.1, U3.1, U3.2, U4.1, U4.3, U12.7, U12.8
/programmer/D+: J6.A6, J14.1, J18.1, U12.3
/programmer/D-: J6.A7, J15.1, J19.1, U12.4
/programmer/RX: U11.P$D5, U12.20
/programmer/TX: U11.P$C5, U12.21
GND: C1.1, C2.2, C3.2, C4.2, C5.2, C6.1, C7.2, C8.2, C9.2, C10.2, C11.2, C12.2, C13.2, C15.2, C16.1, C17.2, C18.2, C19.2, C20.1, C21.2, C22.2, C23.2, C24.2, C25.2, C26.2, C27.2, C28.2, C29.1, C30.1, FB1.2, J3.1, J4.1, J6.A1, J6.A12, J6.B1, J6.B12, J7.3, J7.5, J7.9, J9.1, J23.1, R1.1, R2.2, R5.1, R7.2, R8.2, R12.1, R14.1, R16.1, R19.1, R26.1, R36.2, U1.1, U1.4, U1.6, U1.9, U2.7, U2.12, U2.21, U2.25, U3.6, U3.11, U4.2, U5.2, U5.7, U6.1, U6.6, U6.7, U7.6, U8.2, U8.5, U9.C3, U9.C4, U9.D3, U10.1, U10.2, U10.3, U10.4, U10.7, U11.P$10, U11.P$A0, U11.P$B0, U11.P$C0, U11.P$D0, U12.2, U12.25, U13.6, U14.2
unnamed: C4.1, U2.8
unnamed: C6.2, U2.16
unnamed: C8.1, R37.1, U14.1, U14.3
unnamed: C14.1, C16.2, L2.2
unnamed: C15.1, U9.B5
unnamed: C18.1, U11.P$3, Y1.1
unnamed: C19.1, U11.P$4, Y1.2
unnamed: C22.1, U12.9
unnamed: C28.1, J26.1, U14.5
unnamed: C29.2, J27.4, J29.1, U11.P$8
unnamed: C30.2, J27.2, J28.1, U11.P$7
unnamed: D1.1, U5.5
unnamed: D2.1, U5.4
unnamed: D3.1, U5.3
unnamed: D4.1, R34.2
unnamed: D4.2, U11.P$11
unnamed: D4.4, U11.P$13
unnamed: D5.1, U9.D1
unnamed: D6.1, D6.2, U9.D5
unnamed: D6.3, D6.4, D8.3, D8.4, R36.1, U9.C5
unnamed: D7.1, U9.C1
unnamed: D8.1, D8.2, U9.D4
unnamed: FB1.1, J6.S1
unnamed: L1.1, U2.13
unnamed: L2.1, R31.1, U8.6
unnamed: R1.2, R3.1, U2.9
unnamed: R2.1, U2.20
unnamed: R4.1, R5.2, U2.4
unnamed: R8.1, U3.3
unnamed: R9.1, U3.4
unnamed: R12.2, R13.2, U2.3
unnamed: R14.2, R15.2, U2.6
unnamed: R16.2, R17.2, U2.5
unnamed: R18.1, R22.2, U3.9
unnamed: R19.2, R21.2, U2.2
unnamed: R22.1, U3.8
unnamed: R26.2, U7.12
unnamed: R32.2, U10.5, U11.P$1
unnamed: R33.2, U10.6, U11.P$2
unnamed: R35.1, U13.1

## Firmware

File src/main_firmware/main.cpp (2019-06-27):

#include <stdint.h>

#include "nordic_common.h"
#include "nrf.h"
#include "nrf_sdm.h"
#include "app_error.h"
#include "nrf_sdh.h"
#include "nrf_sdh_soc.h"
#include "app_timer.h"

#include "nrfx_gpiote.h"
#include "nrfx_twim.h"
#include "nrf_delay.h"
#include "nrf_drv_timer.h"

#include "ble.h"
#include "ble_err.h"
#include "ble_hci.h"
#include "ble_srv_common.h"
#include "ble_advdata.h"
#include "ble_advertising.h"
#include "ble_bas.h"
#include "ble_hrs.h"
#include "ble_hts.h"
#include "ble_dis.h"
#include "ble_conn_params.h"
#include "nrf_sdh_ble.h"
#include "peer_manager.h"
#include "peer_manager_handler.h"
#include "fds.h"
#include "nrf_ble_gatt.h"
#include "nrf_ble_lesc.h"
#include "nrf_ble_qwr.h"
#include "ble_conn_state.h"

#include "sensorsim.h"


extern "C" {
  #include "nrf_pwr_mgmt.h"
}


#include "nfc_t2t_lib.h"
#include "nfc_launchapp_rec.h"
#include "nfc_launchapp_msg.h"
#include "nfc_ndef_msg.h"
#include "nfc_text_rec.h"
#include "nfc_uri_msg.h"

#include "nrf_log.h"
#include "nrf_log_ctrl.h"
#include "nrf_log_default_backends.h"
#include "arm_const_structs.h"


#include "BH1792GLC.h"
#include "BH1792GLC_registers.h"

#include "i2c.h"

#include "D4.h"

#include "lsm6dsl_reg.h"

#include "p24_service.h"



#define DEVICE_NAME                         "P24"                            /**< Name of device. Will be included in the advertising data. */
#define MANUFACTURER_NAME                   "Patient24"                   /**< Manufacturer. Will be passed to Device Information Service. */
#define APP_ADV_INTERVAL                    300                                     /**< The advertising interval (in units of 0.625 ms. This value corresponds to 187.5 ms). */

#define APP_ADV_DURATION                    18000                                   /**< The advertising duration (180 seconds) in units of 10 milliseconds. */

#define APP_BLE_CONN_CFG_TAG                1                                       /**< A tag identifying the SoftDevice BLE configuration. */
#define APP_BLE_OBSERVER_PRIO               3                                       /**< Application's BLE observer priority. You shouldn't need to modify this value. */

#define BATTERY_LEVEL_MEAS_INTERVAL         APP_TIMER_TICKS(2000)                   /**< Battery level measurement interval (ticks). */
#define MIN_BATTERY_LEVEL                   81                                      /**< Minimum simulated battery level. */
#define MAX_BATTERY_LEVEL                   100                                     /**< Maximum simulated 7battery level. */
#define BATTERY_LEVEL_INCREMENT             1                                       /**< Increment between each simulated battery level measurement. */

#define HEART_RATE_MEAS_INTERVAL            APP_TIMER_TICKS(2000)                   /**< Heart rate measurement interval (ticks). */
#define PPG_INTERVAL                        APP_TIMER_TICKS(14000)


#define RR_INTERVAL_INTERVAL                APP_TIMER_TICKS(300)                    /**< RR interval interval (ticks). */
#define MIN_RR_INTERVAL                     100                                     /**< Minimum RR interval as returned by the simulated measurement function. */
#define MAX_RR_INTERVAL                     500                                     /**< Maximum RR interval as returned by the simulated measurement function. */
#define RR_INTERVAL_INCREMENT               1                                       /**< Value by which the RR interval is incremented/decremented for each call to the simulated measurement function. */

#define SENSOR_CONTACT_DETECTED_INTERVAL    APP_TIMER_TICKS(5000)                   /**< Sensor Contact Detected toggle interval (ticks). */

#define MIN_CONN_INTERVAL                   MSEC_TO_UNITS(400, UNIT_1_25_MS)        /**< Minimum acceptable connection interval (0.4 seconds). */
#define MAX_CONN_INTERVAL                   MSEC_TO_UNITS(650, UNIT_1_25_MS)        /**< Maximum acceptable connection interval (0.65 second). */
#define SLAVE_LATENCY                       0                                       /**< Slave latency. */
#define CONN_SUP_TIMEOUT                    MSEC_TO_UNITS(4000, UNIT_10_MS)         /**< Connection supervisory timeout (4 seconds). */

#define FIRST_CONN_PARAMS_UPDATE_DELAY      APP_TIMER_TICKS(5000)                   /**< Time from initiating event (connect or start of notification) to first time sd_ble_gap_conn_param_update is called (5 seconds). */
#define NEXT_CONN_PARAMS_UPDATE_DELAY       APP_TIMER_TICKS(30000)                  /**< Time between each call to sd_ble_gap_conn_param_update after the first call (30 seconds). */
#define MAX_CONN_PARAMS_UPDATE_COUNT        3                                       /**< Number of attempts before giving up the connection parameter negotiation. */

#define LESC_DEBUG_MODE                     0                                       /**< Set to 1 to use LESC debug keys, allows you to use a sniffer to inspect traffic. */

#define SEC_PARAM_BOND                      1                                       /**< Perform bonding. */
#define SEC_PARAM_MITM                      0                                       /**< Man In The Middle protection not required. */
#define SEC_PARAM_LESC                      1                                       /**< LE Secure Connections enabled. */
#define SEC_PARAM_KEYPRESS                  0                                       /**< Keypress notifications not enabled. */
#define SEC_PARAM_IO_CAPABILITIES           BLE_GAP_IO_CAPS_NONE                    /**< No I/O capabilities. */
#define SEC_PARAM_OOB                       0                                       /**< Out Of Band data not available. */
#define SEC_PARAM_MIN_KEY_SIZE              7                                       /**< Minimum encryption key size. */
#define SEC_PARAM_MAX_KEY_SIZE              16                                      /**< Maximum encryption key size. */

#define DEAD_BEEF                           0xDEADBEEF                              /**< Value used as error code on stack dump, can be used to identify stack location on stack unwind. */


#define TEMP_TYPE_AS_CHARACTERISTIC     0                                           /**< Determines if temperature type is given as characteristic (1) or as a field of measurement (0). */


#define FPU_EXCEPTION_MASK 0x0000009F
#define FPU_FPSCR_REG_STACK_OFF 0x40



BLE_HRS_DEF(m_hrs);                                                 /**< Heart rate service instance. */
BLE_HTS_DEF(m_hts);                                                                 /**< Structure used to identify the health thermometer service. */
BLE_BAS_DEF(m_bas);                                                 /**< Structure used to identify the battery service. */
NRF_BLE_GATT_DEF(m_gatt);                                           /**< GATT module instance. */
NRF_BLE_QWR_DEF(m_qwr);                                             /**< Context for the Queued Write module.*/
ble_p24_t m_p24_service;                                            //p24_service

BLE_ADVERTISING_DEF(m_advertising);                                 /**< Advertising module instance. */
APP_TIMER_DEF(m_battery_timer_id);                                  /**< Battery timer. */
APP_TIMER_DEF(m_heart_rate_timer_id);                               /**< Heart rate measurement timer. */
APP_TIMER_DEF(m_rr_interval_timer_id);                              /**< RR interval timer. */
APP_TIMER_DEF(m_sensor_contact_timer_id);                           /**< Sensor contact detected timer. */
APP_TIMER_DEF(m_ppg_timer_id);

static uint16_t m_conn_handle         = BLE_CONN_HANDLE_INVALID;    /**< Handle of the current connection. */
static bool     m_rr_interval_enabled = true;                       /**< Flag for enabling and disabling the registration of new RR interval measurements (the purpose of disabling this is just to test sending HRM without RR interval data. */

static bool              m_hts_meas_ind_conf_pending = false;                       /**< Flag to keep track of when an indication confirmation is pending. */


static sensorsim_cfg_t   m_battery_sim_cfg;                         /**< Battery Level sensor simulator configuration. */
static sensorsim_state_t m_battery_sim_state;                       /**< Battery Level sensor simulator state. */
static sensorsim_cfg_t   m_rr_interval_sim_cfg;                     /**< RR Interval sensor simulator configuration. */
static sensorsim_state_t m_rr_interval_sim_state;                   /**< RR Interval sensor simulator state. */


static ble_uuid_t m_adv_uuids[] =                                   /**< Universally unique service identifiers. */
{
    {BLE_UUID_HEART_RATE_SERVICE,           BLE_UUID_TYPE_BLE},
    {BLE_UUID_BATTERY_SERVICE,              BLE_UUID_TYPE_BLE},
    {BLE_UUID_DEVICE_INFORMATION_SERVICE,   BLE_UUID_TYPE_BLE},
    {BLE_UUID_HEALTH_THERMOMETER_SERVICE,   BLE_UUID_TYPE_BLE},
    {BLE_UUID_P24_SERVICE_UUID,    BLE_UUID_TYPE_VENDOR_BEGIN}
};


#define BH1792_INT_PIN     15

/* TWI instance ID. */
#define TWI_INSTANCE_ID     0

#define FPU_EXCEPTION_MASK               0x0000009F                      //!< FPU exception mask used to clear exceptions in FPSCR register.
#define FPU_FPSCR_REG_STACK_OFF 0x40 


/* TWI instance. */
static const nrfx_twim_t m_twi = NRFX_TWIM_INSTANCE(TWI_INSTANCE_ID);

static const I2C m_i2c = I2C(&m_twi);

static const nrfx_timer_t TIMER_PPG_SYNC = NRF_DRV_TIMER_INSTANCE(1);

static uint8_t ctr = 0;

uint32_t previous_tick = 0;
uint32_t current_tick = 0;
static uint16_t step_count = 0;


static axis3bit16_t data_raw_acceleration;
static axis3bit16_t data_raw_angular_rate;
static axis1bit16_t data_raw_temperature;
static float acceleration_mg[3];
static float angular_rate_mdps[3];
static float temperature_degC;
static uint8_t whoamI, rst;
static lsm6dsl_ctx_t dev_ctx;
static lsm6dsl_int1_route_t step;
lsm6dsl_ctrl10_c_t enable_func;
lsm6dsl_ctrl10_c_t enable_ped;
static mems_status_t error = MEMS_ERROR;



static lsm6dsl_func_cfg_access_t access_me;

//static const nrf_drv_spi_t spi = NRF_DRV_SPI_INSTANCE(0);

/************************************************************SH*****************************************************/
static float _x_last_odr = 26.0f;
static uint8_t _x_is_enabled = 0;

//NRF_ATFIFO_DEF(sample_fifo, uint16_t, 1116U);

static float32_t samples[1024];
static float32_t PSD[1024];
static uint16_t sample_counter = 0;

BH1792GLC m_bh1792 = BH1792GLC(&m_i2c);


static bool sensor_contact_detected = true;
static bool bh_finished = true;
static bool bh_started = false;
static uint8_t heart_rate = 0;



static arm_rfft_fast_instance_f32 fft_instance;
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

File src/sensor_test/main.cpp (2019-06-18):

/**
 * Copyright (c) 2014 - 2019, Nordic Semiconductor ASA
 *
 * All rights reserved.
 *
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
 * 3. Neither the name of Nordic Semiconductor ASA nor the names of its
 *    contributors may be used to endorse or promote products derived from this
 *    software without specific prior written permission.
 *
 * 4. This software, with or without modification, must only be used with a
 *    Nordic Semiconductor ASA integrated circuit.
 *
 * 5. Any software provided in binary form under this license must not be reverse
 *    engineered, decompiled, modified and/or disassembled.
 *
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
 */
/** @example examples/ble_peripheral/ble_app_hrs/main.c
 *
 * @brief Heart Rate Service Sample Application main file.
 *
 * This file contains the source code for a sample application using the Heart Rate service
 * (and also Battery and Device Information services). This application uses the
 * @ref srvlib_conn_params module.
 */

#include <stdint.h>
#include <string>
#include <vector>
#include <iterator>

#include "nordic_common.h"
#include "nrf.h"
#include "nrf_sdm.h"
#include "app_error.h"
#include "ble.h"
#include "ble_err.h"
#include "ble_hci.h"
#include "ble_srv_common.h"
#include "ble_advdata.h"
#include "ble_advertising.h"
#include "ble_bas.h"
#include "ble_hrs.h"
#include "ble_dis.h"
#include "ble_conn_params.h"
#include "sensorsim.h"
#include "nrf_sdh.h"
#include "nrf_sdh_ble.h"
#include "nrf_sdh_soc.h"
#include "app_timer.h"
#include "bsp_btn_ble.h"
#include "peer_manager.h"
#include "peer_manager_handler.h"
#include "fds.h"
#include "nrf_ble_gatt.h"
#include "nrf_ble_lesc.h"
#include "nrf_ble_qwr.h"
#include "ble_conn_state.h"
#include "nrf_atfifo.h"

#include "nrf.h"
#include "nrf_drv_gpiote.h"
#include "nrfx_gpiote.h"
#include "nrfx_twim.h"
#include "nrf_delay.h"
#include "nrf_drv_timer.h"
//#include "arm_const_structs.h"


extern "C" {
  #include "nrf_pwr_mgmt.h"
}

#include "BH1792GLC.h"
#include "BH1792GLC_registers.h"

#include "i2c.h"
#include "lsm6dsl_reg.h"

#include "nrf_log.h"
#include "nrf_log_ctrl.h"
#include "nrf_log_default_backends.h"


#define DEVICE_NAME                         "Nordic_HRM"                            /**< Name of device. Will be included in the advertising data. */
#define MANUFACTURER_NAME                   "NordicSemiconductor"                   /**< Manufacturer. Will be passed to Device Information Service. */
#define APP_ADV_INTERVAL                    300                                     /**< The advertising interval (in units of 0.625 ms. This value corresponds to 187.5 ms). */

#define APP_ADV_DURATION                    18000                                   /**< The advertising duration (180 seconds) in units of 10 milliseconds. */

#define APP_BLE_CONN_CFG_TAG                1                                       /**< A tag identifying the SoftDevice BLE configuration. */
#define APP_BLE_OBSERVER_PRIO               3                                       /**< Application's BLE observer priority. You shouldn't need to modify this value. */

#define BATTERY_LEVEL_MEAS_INTERVAL         APP_TIMER_TICKS(2000)                   /**< Battery level measurement interval (ticks). */
#define MIN_BATTERY_LEVEL                   81                                      /**< Minimum simulated battery level. */
#define MAX_BATTERY_LEVEL                   100                                     /**< Maximum simulated 7battery level. */
#define BATTERY_LEVEL_INCREMENT             1                                       /**< Increment between each simulated battery level measurement. */

#define HEART_RATE_MEAS_INTERVAL            APP_TIMER_TICKS(1000)                   /**< Heart rate measurement interval (ticks). */
#define MIN_HEART_RATE                      140                                     /**< Minimum heart rate as returned by the simulated measurement function. */
#define MAX_HEART_RATE                      300                                     /**< Maximum heart rate as returned by the simulated measurement function. */
#define HEART_RATE_INCREMENT                10                                      /**< Value by which the heart rate is incremented/decremented for each call to the simulated measurement function. */
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

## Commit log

2019-05-06 Initial commit with hardware
    [HealthMonitor.kicad_pcb, HealthMonitor.sch]
2019-05-06 Created sheet hierarchy"
    [HealthMonitor.sch, bh1792-interface.sch]
2019-05-06 IMU sensor
    [IMUSensor.sch]
2019-05-09 Created Power PCB, both schematic and layout
    [HealthMonitor.kicad_pcb, HealthMonitor.sch, bh1792-interface.sch, power.sch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]
2019-05-15 Finished PCB Draft -- waiting for review
    [HealthMonitor.kicad_pcb, HealthMonitor.sch, IMUSensor.sch, Max86141.sch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]
2019-05-16 Fixed most DRC errors, remaining errors should be fine
    [HealthMonitor.kicad_pcb]
2019-05-16 Moved test point to reduce the length of the LED lead
    [HealthMonitor.kicad_pcb]
2019-05-16 Generated gerbers
    [HealthMonitor-B.Cu.gbl, HealthMonitor-B.Mask.gbs, HealthMonitor-B.Paste.gbp, HealthMonitor-B.SilkS.gbo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]
2019-05-20 Updated PCB and generated gerbers
    [HealthMonitor.kicad_pcb, HealthMonitor.xlsx, MaxSensorComplete.sch]
2019-05-22 Refactored currently existing code Finished BH1792GLC library
    [HealthMonitor-B.Paste.dxf, HealthMonitor-F.Paste.dxf, HealthMonitor.kicad_pcb]
2019-06-03 rescue commit
    [ABS06-v2.step, ADG884BRMZ.step, ADP5092.step, BH1792.STEP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]
2019-06-07 sensor test
2019-06-10 latest design
    [HealthMonitor-B_CrtYd.gbr, HealthMonitor-B_Cu.gbl, HealthMonitor-B_Mask.gbs, HealthMonitor-B_Paste.gbp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]
2019-06-18 Final version of the firmware code
    [HealthMonitor.kicad_pcb, MaxSensorComplete.sch]
2019-06-20 Demo firmware code
    [power.sch]
2019-06-21 Version at demo
    [power.sch]
2019-06-22 Pedometer, temperature, and raw accelerometer vals
    Pedometer, temperature, and raw accelerometer vals
2019-06-23 Components for boards
    [Bill of Materials.xlsx]
2019-06-23 BOM for PCBs
    [Bill of Materials.xlsx]
2019-06-23 Sample of Team Minutes
2019-06-27 strap pictures

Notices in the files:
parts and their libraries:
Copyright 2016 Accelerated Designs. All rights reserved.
